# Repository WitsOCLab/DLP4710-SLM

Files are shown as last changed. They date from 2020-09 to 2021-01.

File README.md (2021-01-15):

# DLP4710-SLM
A 3D printed modification to the DLP4710EVM DMD to turn it into a lab-usable spatial light modulator. Optimised example MATLAB code for displaying Laguerre-Gauss holograms fullscreen are in the Examples folder.

**Created by:** Mitchell A. Cox in 2020 :: www.wits.ac.za/eie [mitchell.cox@wits.ac.za]

**License:** CC-BY-SA-4.0

## Reference

Please note that build instructions, photos, etc. are in the following paper:

M. A. Cox, A. V. Drozdov, "Converting a Texas Instruments DLP4710 DLP evaluation module into a spatial light modulator," Applied Optics, in press.

If you find this work useful, please consider citing or acknowledging it. If you make improvements, please send a pull request.

## 3D Printer Settings

The designs have been verified with an Ultimaker S3 using Cura with the following settings:

> **Layer height:** 0.1 mm
> **Infill:** 80%
> **Adhesion:** No
> **Support:** No
> **Material:** Black Strong PLA

**If you have been successful with other printers / settings, please let me know.**

## Errata / ProTips

* The DMD is quite a tight squeeze into the face-plate.

## Useful URLs

https://www.ti.com/tool/DLPDLCR4710EVM-G2

https://www.ti.com/tool/DLP4710EVM-LC

## Updating the Firmware

Some firmware updating is required so that the LEDs are disabled on start (otherwise it won't turn on as it thinks the LEDs are broken) and to set the input source to the HDMI port.

For some reason the Texas Instruments software for the DLP4710-G2 evaluation board doesn't update the firmware. It says it does, but it doesn't (it's pretty clear that nothing happens as it's too quick when one tries). Instead, the software meant for the DLP4710-LC must be used. It will complain about the wrong board, but it still works. The screenshot below shown the place where this should be done and how it looks.

A firmware image can be download from the TI product page. A batch file to switch off the LEDs and set the input is in the "Firmware" directory. Please note that if you try to flash the wrong firmware or if something goes wrong, it's at your own risk.

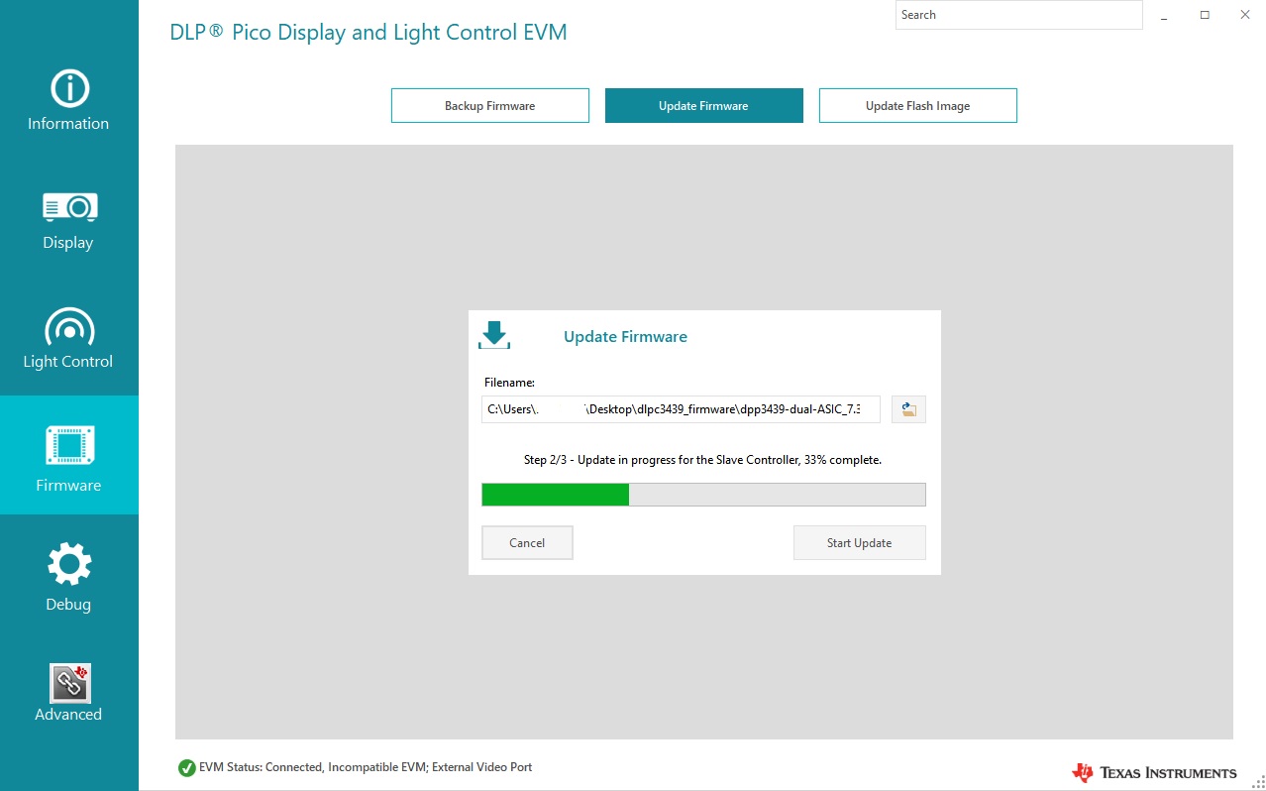
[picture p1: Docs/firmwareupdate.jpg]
DLP4710LC Update Screenshot


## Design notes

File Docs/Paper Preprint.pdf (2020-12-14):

Letter | Applied Optics | 1

# Converting a Texas Instruments DLP4710 DLP evaluation module into a spatial light modulator

MITCHELL A. COX1,* AND ALICE V. DROZDOV1

1School of Electrical and Information Engineering, University of the Witwatersrand, Johannesburg, South Africa *Corresponding author: mitchell.cox@wits.ac.za

Compiled December 14, 2020

Digital Micro-mirror Devices (DMDs) are a popular alternative to liquid crystal spatial light modulators for laser beam shaping due to their relatively low cost, high speed, as well as polarisation and wavelength independence. Here we describe in detail how to convert a low-cost digital light projector (DLP) evaluation module which uses a Texas Instruments DLP4710 DMD into a spatial light modulator using a 3D printed mount. The resulting device is shown to accurately shape Laguerre-Gauss modes, can operate in real-time over HDMI without modification with a 180 Hz hologram refresh rate, has a resolution of 1920×1080 pixels and a diagonal screen size of 0.47 inches.

http://dx.doi.org/10.1364/ao.XX.XXXXXX

### 1. INTRODUCTION

Digital Micro-mirror Devices (DMDs) were developed in the 1980s and 1990s and are now primarily used in digital movie projectors due to their high-contrast and high-power handling capabilities [1]. More recently, they have become a useful experimental tool that are now used in various optics experiments and applications such as structured light, microscopy, photolithography and single pixel imaging to name a few [2–8]. Here we focus on the use of DMDs as polarisation and wavelength invariant computer generated holograms for structured light applications such as mode creation and detection, wavefront sensing and polarimetry [9–14]. The presented arrangement, however, is such that the DMD may find use in many other applications.
A DMD is a 2D array of micro-mirrors spaced several micrometers apart with the ability to be electronically tilted to an “on” or “off” position, usually to direct incident light toward or away from a target [12]. The resolution of modern DMDs is on the order of hundreds or even thousands of pixels in each dimension. Typically, the available resolutions follow common display standards and so 1920×1080 (Full HD) is readily available, but higher and lower resolutions are available (at higher or lower cost).
In order to use a DMD as a so-called spatial light modulator, the bare DMD must be situated such that an incident laser beam and required experimental components can be conveniently

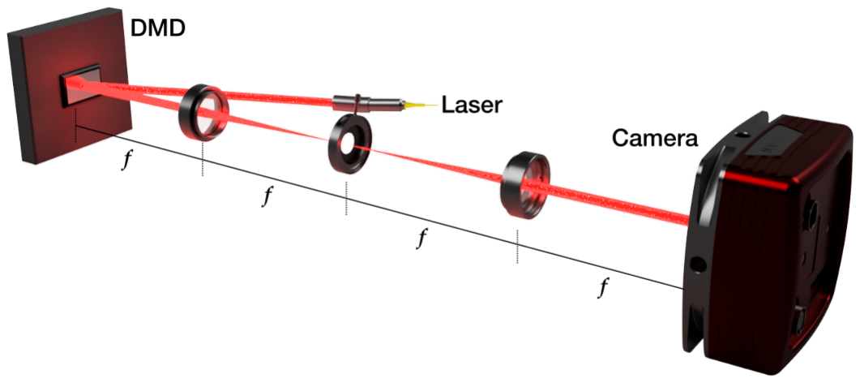
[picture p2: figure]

Fig. 1. A typical experimental layout with a single mode fibrebased laser source, a DMD, a spatial filter and a camera. For the demonstration tests presented here we used f = 100 mm lenses and a 635 nm single-mode coupled laser diode source collimated to a beam diameter of 2.1 mm.

located. Some DMD development modules are sold without optics such as the Texas Instruments DLP 6500 EValuation Modules (EVM) [15] and DLP Discovery 4100 Development Platform [16], and are usable with a custom mount and no further modification. Here we focus instead on the Texas Instruments DLPDLCR4710EVM-G2 which is significantly cheaper (and thus more accessible to researchers with a tighter budget) than other DMD evaluation modules currently available, while also having specifications highly conducive to structured light experiments [17]. A physically similar module, the DLP4710EVM-LC is also expected to work using the modifications described here [18]. Unfortunately, both DLP4710 EVM models have pre-installed projection optics which must be removed before they can be used.
In Sec. 2, a typical experimental setup for mode creation is provided, as well as a brief summary of how holograms for DMDs can be created with references to some tutorial papers for the interested reader. This setup and generation method is used to test the performance of the modified DLP4710 EVM with some test results also presented. Section 3 details the required modifications, 3D printed components and firmware configuration to use the DLP4710 EVM as a spatial light modulator.

### 2. SHAPING LIGHT WITH A DMD

Since the DMD can be re-purposed as a digital hologram, it can be used to structure light, with a comprehensive tutorial in

Ref. [12]. It is out of the scope of this paper to go into detail on the various possible techniques to do this, but for the purposes of demonstrating a working device, some brief background is given in this section.
A minimal experimental setup is shown in Fig. 1, where a collimated Gaussian laser beam is reflected off the DMD, where the first-order is then spatially filtered using a 4 f-system using an adjustable iris aperture and finally imaged using a camera. We use this setup to test and demonstrate the capabilities of the DLP4710 DMD, described in Sec. 4.
A DMD is an amplitude-only device and cannot inherently modulate the phase of light, which is required for complex beam shaping. In order to encode a field with both amplitude and phase components a special grating function is used to create a binary, amplitude-only hologram [12, 19]. The transmission function of this type of hologram is given by

T =

1
2

+

1
2

sgn

cos(2πψG + ψU) + cos

arcsin
A

Amax , (1)

where ψU and A/Amax are the phase and normalised amplitude of the desired complex field, U, respectively (for example Eq. 2, which describes a Laguerre-Gauss (LG) mode) and ψG is a linear phase ramp which defines the period of the resulting grating. Examples of what the binary holograms look like with LG modes are shown in Fig. 5 (a).
LG modes are solutions to the scalar Helmholtz equation in cylindrical coordinates [20]. They form an orthonormal basis and are also Eigenmodes of free-space, making them useful for long-distance propagation, for example in multiplexed wireless optical communication [21]. At the plane of the DMD (i.e z = 0) they are given by

U

LG
`,p

(r, φ) = C

LG

r

√
2
w0

!|`|
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
exp(−i`φ),

(2)
where ` and p are the azimuthal and radial mode indices respectively, w0 is the beam waist, C

LG is a normalisation constant and L

|`|
p (·) is the generalised Laguerre polynomial.
LG modes are identifiable as they appear as donut-shaped rings on a camera in a setup such as in Fig. 1. Larger azimuthal indices result in larger diameter rings and radial modes manifest as rings around the bright, central ring. Even small aberrations on the surface of the DMD will result in these rings becoming distorted. This is a convenient qualitative measure of the DMDs beam shaping performance.
If the resulting beam quality is insufficient, a correction phase can be added or subtracted to the hologram. The Gerchberg-Saxton algorithm can be used to find this phase, or alternatively, suitable Zernike phases can be added or subtracted in a “trialand-error” manner [10]. As a last resort, one can reduce the size of the encoded beams to limit the exposure to the aberrated area.

### 3. HARDWARE AND FIRMWARE

The DLP4710 DMD from Texas Instruments has an array size of 1920×1080 pixels with a pixel pitch of 5.4 µm. This results in an active array size of 10.4×5.8 mm (or 0.47 inch diagonal). The DMD is available on two affordable evaluation modules, both of which can be modified for laser-based experiments. In this work the DLPDLCR4710EVM-G2 was used, but the DLP4710EVM-LC appears to have the same dimensions as it seems that only a different chipset is used (See. Sec. C) [17, 18].

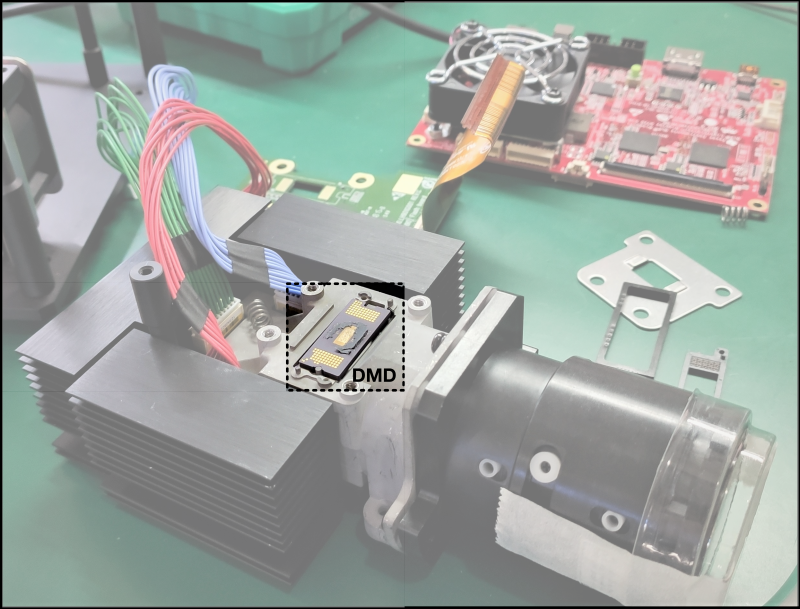
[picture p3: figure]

Fig. 2. A photo of the DLP4710 EVM with the main PCB removed, showing the un-soldered DMD positioned in the projection optics module.

The 3D printed assembly is described in Sec. 3A, as well as some firmware configuration changes, described in Sec. 3B. Holograms are displayed on the DMD via the HDMI connection, as the EVM simply shows up as another monitor. We describe how to display holograms at a rate of 180 Hz over HDMI in Sec. 3C.

A. 3D Printed Assembly
There are two reasons why a custom mounting assembly is required for the DLPDLCR4710EVM-G2. The first is that the bare DMD chip must be positioned vertically at a height that is suitable for standard laser-based setups. Unfortunately, the DLP4710 DMD is not soldered to the board in this EVM and so simply stripping away the projection optics is not an option. A precise assembly is thus required to hold all the components in alignment.
As is visible in Fig. 2, the DMD is precisely slotted into the projection optics and uses a spring-loaded inter-poser shim for the electrical signals to a PCB (Printed Circuit Board) which is screwed down with heat-sinks to hold everything in place. A precision assembly is therefore required to hold the DMD in place on the circuit board in the absence of the projection optics. A photo of the custom assembly is shown in Fig. 3 (a) and (d). Two plastic components must be printed at high resolution. Here an Ultimaker S3 at 0.1 mm layer height with “Strong PLA” filament and 80% infill was used to create a rigid and accurate structure. Figure 3 (b) shows the mount plate, which holds everything in position and allows for a standard M6 cap screw and optical post to be attached. Figure 3 (c) shows the more intricate cover plate, which has “pins” to hold the DMD, shim and PCB in precise alignment. No additional screws or hardware are required as the design is such that the existing screws and springs from the EVM can be used, as shown. The design caters for M3 nuts on the front of the cover plate for added strength and reliability, if required. The design files in both STEP and STL formats are available online [22].

To assemble, carefully slot the DMD face-down into the cover plate, then the shim and then place the PCB. Everything should slot into place. The square-shaped metal plate is placed behind

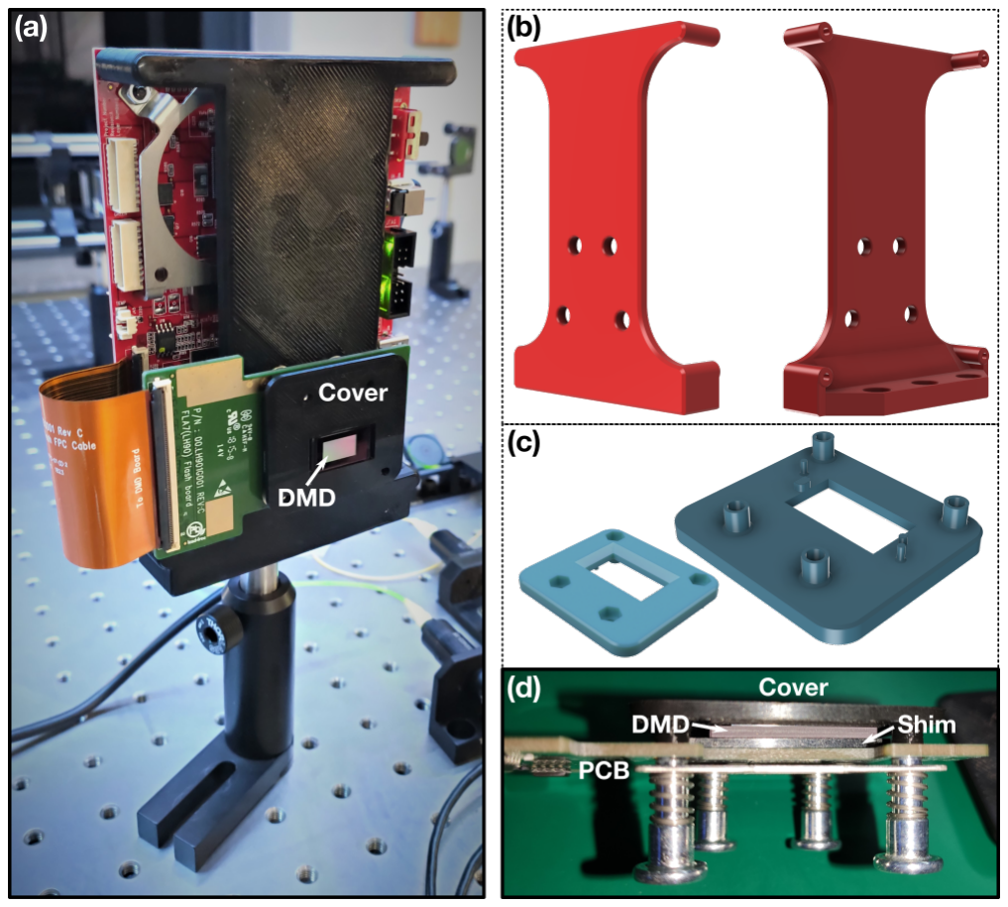
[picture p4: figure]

Fig. 3. A photo of the completed unit (a), with renderings of the 3D printed mount (b) and DMD cover (c). The key component is the cover, which has several alignment pins to hold the DMD, inter-poser shim and PCB in exact position (d).

the PCB, as it was before the DMD was removed from the light engine. Figure 3 (d) shows the resulting arrangement. In reality, the assembly requires the screws to be inserted through the mount plate (Figure 3 (b)) first, after which the springs are placed. While holding everything together in position, gently and carefully turn the screws so that they grab the cover plate. Incrementally tighten diagonally opposite screws until the assembly is rigid.
Do not over-tighten these screws as the plastic can be stripped. There is also a possibility that the DMD is warped if things are too tight, but the use of the shim largely prevents this, ensuring optical flatness. It should also be noted that there is a specified maximum clamping load of 110 N (Sec. 6.9 in the DLP4710 datasheet), but we are unable to verify this and assume that this load is not exceeded as the original clamping springs are used. Remove the fan from the top of the main board. This is not required as the LED driver circuit will not generate any heat with no LEDs connected. There should now be space to mount the cover assembly to the main PCB. Use the remaining screws to assemble everything as shown in Figure 3 (a). During this entire procedure, be careful of electrostatic discharge. A grounded wrist strap is recommended, and working on a grounded metal table or anti-static matt is also a good idea.
B. Firmware Configuration
By default, the firmware expects there to be LEDs connected. The module will not power on correctly if it detects that these LEDs are not present. In addition, the default mode of the device is to display a demo graphic and so this must be changed to the HDMI input. Fortunately, the configuration can be modified and saved into non-volatile memory.
Download and install the configuration utility from the DLP4710EVM product page [17]. Instructions are available from Texas Instruments to do this, and how to troubleshoot any issues that may arise. Using the utility, a so-called “batch file” can be created and flashed to the EVM to update the configuration on

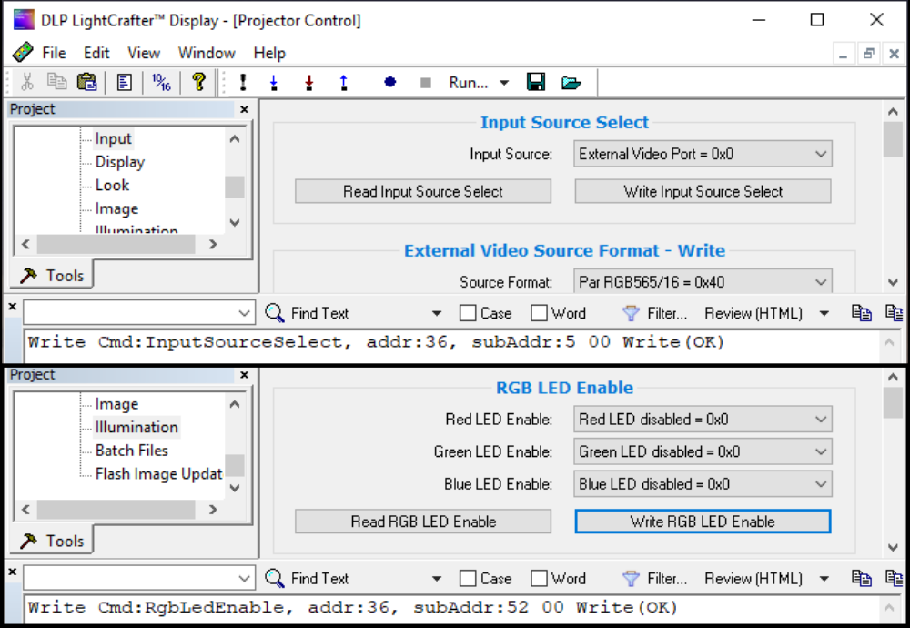
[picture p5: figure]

Fig. 4. Screenshots of the configuration utility in Advanced mode showing the HDMI source selection (top) and LED disable configuration (inset bottom).

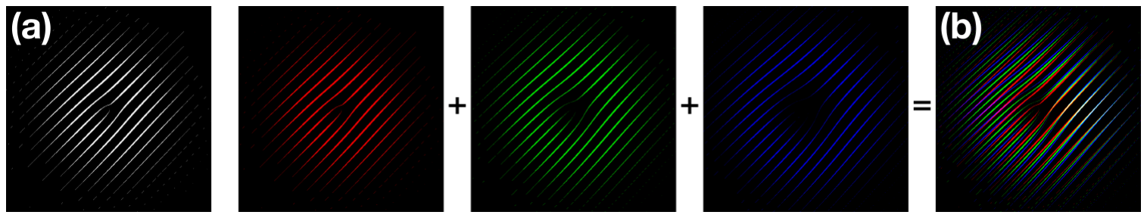
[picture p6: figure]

Fig. 5. (a) A typical binary hologram for a DMD of an LG,
` = 1 hologram for up to 60 Hz operation over HDMI. (b) The resulting hologram image with three consecutive LG holograms with ` = 1, 2 and 3 for 180 Hz operation.

startup.
The contents of this batch file, which is simply a text file with the extension “.bf”, are shown in Lst. 1. The specifics of how to install this file into non-volatile memory is left to the reader as the instructions are available from the manufacturer. For convenience, Fig. 4 shows a series of screenshots of the configuration utility highlighting the LED and input source configuration which can be done after the DMD is turned on, if the batch file method is not desired.
1 | # Write : InputSourceSelect
2 | W 36 05 00
3 | # Write : RgbLedEnable
4 | W 36 52 00
Listing 1. Batch file contents for the DLPDLCR4710EVM-G2 to disable the LEDs and switch to the HDMI input.
C. High Speed Display over HDMI
The specified frame-rate of the DLP4710 EVMs is 60 Hz over HDMI, and so holograms can be displayed at this rate without any special techniques. As an aside, the DLP4710 DMD itself supports 120 Hz and so the 60 Hz limitation is due to the chipset and firmware. Screen tearing or missed frames might occur at rates close to this frequency unless synchronisation to the screen refresh rate is used. Techniques to do this depend on the software and operating system and will not be detailed here. With an understanding of how the DMD modulates the Red (R), Green (G) and Blue (B) channels for 24 bit colour, we can in fact display different binary holograms at a rate of 180 Hz or even 1440 Hz [23]. Here we describe how to update the DMD at 180 Hz as no special configuration is required to do so. It should be noted that some DMD EVMs support the loading

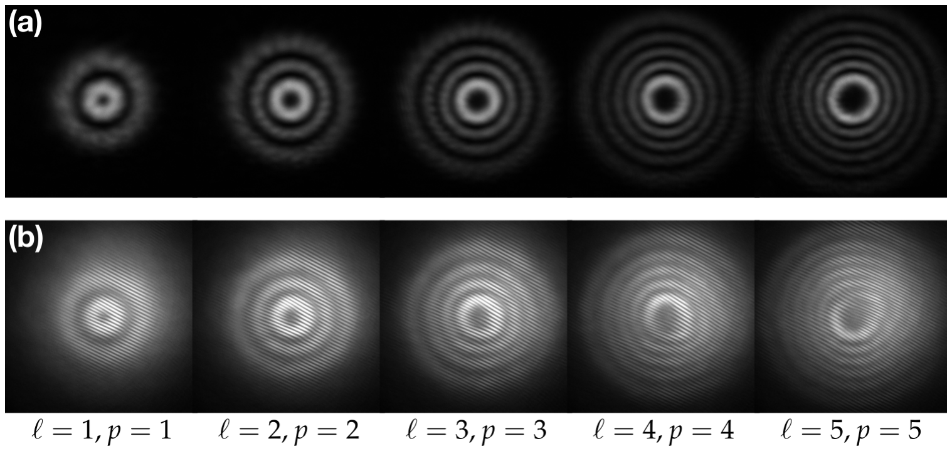
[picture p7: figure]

Fig. 6. (a) Example LG beams generated using the device with slight aberrations visible as deviations from a round shape confirmed by (b) which are Mach-Zehnder interferograms of the beams showing some curvature of the fringes and vortex splitting. The intensity variations in (a) are due to a suboptimal grating period and possibly some interference with the zero-order, which could be removed with a smaller spatial filter.

of images into the DMDs memory and playing them back at several kilohertz. This mode of operation is not supported on the DLPDLCR4710EVM-G2.
The DMD rapidly switches between the red, green and blue channels while synchronously toggling the corresponding coloured LEDs, to create the perception of a colour image. A black and white image is in fact displayed as three separate, sequential frames: the first is black and red, then black and green and finally black and blue. By encoding different holograms (or images) as each of these three colours and then merging them into a single image, the resulting “effective” rate is 180 Hz (if these images are displayed at 60 Hz). Figure 5 (b) diagrammatically shows what the displayed hologram might look like. As an example, Lst. 2 shows the MATLAB code to generate this RGB image from three binary images, since colour images in MATLAB are represented as 3D matrices. Example code for demonstrating this technique, as well as for displaying these colour images full screen as holograms on the EVM, is provided online [22].
1 | function [ imgCombined ] = Combine180 ( imgA , imgB , imgC )
2 | imgCombined = cat (3 , imgA , imgB , imgC );
3 | end
Listing 2. Generating a combined image to achieve 180 Hz hologram rate.

### 4. TEST RESULTS AND DISCUSSION

In order to perform a rudimentary test of the performance of this DMD, LG modes were generated with ` ∈ [−5, 5] and p ∈ [0, 5], with the code available online [22], using a similar setup to that given in Fig. 1. The incoming beam had a 1/e

2 diameter of
2.1 mm and the encoded beams had w0 = 1 mm.
The holograms for each mode were generated, displayed on the DMD and then the resulting beam was captured with a camera. These images were inspected and the modes are high quality. Figure 6 (a) shows a selection of images of these modes. Some distortion is visible on the largest mode, indicative of minor aberrations.
This is confirmed by the interferograms shown in Fig. 6 (b), generated by interfering the incoming Gaussian beam with the resulting mode. The fringes on the interferograms should be straight, with a fork at the centre with a number of “tines” depending on `. Some curvature is visible as well as some vortex splitting. While taking these measurements we noted that the mount is quite sensitive to vibrations. This is due to the vertical arrangement and the low rigidity of the plastic. The design was modified to increase the rigidity and in future versions we plan to improve it further.
We speculate that the relatively insignificant aberrations of this particular DMD (compared to the DLP6500 used by one of the authors previously [9]) are due to two reasons. The first is it’s relatively small size which limits bending. Second, we believe that the main reason for the high flatness of this DMD is because it is not soldered down. It is possible that the process of soldering the DMD causes differential expansion and contraction as the solder cools, deforming the DMD. In a projection setup these aberrations would be of no consequence, but for beam shaping a fraction of the wavelength has an impact.
High speed operation at 180 Hz was also verified by combining three different LG beams into a single RGB image and observing the laser beam using a camera running at 500 Hz. Unfortunately there is no output trigger signal on the DLPDLCR4710EVM-G2 which could have been used to trigger the camera in sync to the frame changes, and so oversampling was necessary. If this signal is required, it is available on the DLP4710EVM-LC, according to the datasheet.

### 5. SUMMARY

Spatial light modulators have become a staple component in laser optics labs working with structured light. Digital micromirror devices are versatile, fast and affordable and are an excellent alternative to conventional liquid crystal spatial light modulators. DMDs are not yet available as off-the-shelf as scientific instruments and so evaluation kits usually in the form of digital projectors must be purchased and modified.
We explain in detail how the Texas Instruments DLP4710 evaluation modules can be modified for laser beam shaping with some 3D printed components and firmware configuration. We visually tested the resulting device with a range of LG modes and find the device to be remarkably aberration-free.

FUNDING

The authors would like to acknowledge South African National Research Foundation grant 121908 and the National Laser Centre Rental Pool program.
Disclosures. The author declares no conflicts of interest.

REFERENCES

1. L. J. Hornbeck, “Multi-level deformable mirror device,” (1992). US Patent 5,083,857.
2. T. M. Kreis, P. Aswendt, and R. Höfling, “Hologram reconstruction using a digital micromirror device,” Opt. Eng. 40, 926–933 (2001).
3. D. Dan, M. Lei, B. Yao, W. Wang, M. Winterhalder, A. Zumbusch,
Y. Qi, L. Xia, S. Yan, Y. Yang et al., “DMD-based led-illumination super-resolution and optical sectioning microscopy,” Sci. Rep. 3, 1116 (2013).
4. A. Sandmeyer, M. Lachetta, H. Sandmeyer, W. Hübner, T. Huser, and M. Müller, “DMD-based super-resolution structured illumination microscopy visualizes live cell dynamics at high speed and low cost,” bioRxiv p. 797670 (2019).
5. K. V. Vienola, M. Damodaran, B. Braaf, K. A. Vermeer, and J. F. de Boer, “Parallel line scanning ophthalmoscope for retinal imaging,” Opt. Lett. 40, 5335–5338 (2015).

6. M. P. Edgar, G. M. Gibson, and M. J. Padgett, “Principles and prospects for single-pixel imaging,” Nat. Photonics 13, 13–20 (2019).
7. Z. Xiong, H. Liu, R. Chen, J. Xu, Q. Li, J. Li, and W. Zhang, “Illumination uniformity improvement in digital micromirror device based scanning photolithography system,” Opt. Express 26, 18597–18607 (2018).
8. Y. Zhang, J. Luo, Z. Xiong, H. Liu, L. Wang, Y. Gu, Z. Lu, J. Li, and J. Huang, “User-defined microstructures array fabricated by DMD based multistep lithography with dose modulation,” Opt. Express 27 ,
31956–31966 (2019).
9. M. A. Cox, E. Toninelli, L. Cheng, M. J. Padgett, and A. Forbes, “A High-Speed, Wavelength Invariant, Single-Pixel Wavefront Sensor With a Digital Micromirror Device,” IEEE Access

7, 85860–85866 (2019).
10. J. Pinnell, I. Nape, B. Sephton, M. A. Cox, V. Rodriguez-Fajardo, and
A. Forbes, “Modal analysis of structured light with spatial lightmodulators: a practical tutorial,” J. Opt. Soc. Am. A 37, 146–160 (2020).
11. K. Singh, N. Tabebordbar, A. Forbes, and A. Dudley, “Digital Stokes polarimetry and its application to structured light: tutorial,” J. Opt. Soc. Am. A 37, C33 (2020).
12. S. Scholes, R. Kara, J. Pinnell, V. Rodríguez-Fajardo, and A. Forbes, “Structured light with digital micromirror devices: a guide to best practice,” Opt. Eng. 59, 1 (2019).
13. S. Turtaev, I. T. Leite, K. J. Mitchell, M. J. Padgett, D. B. Phillips, and T. Cižmár, “Comparison of nematic liquid-crystal and DMD based ˇ spatial light modulation in complex photonics,” Opt. Express 25, 29874– 29884 (2017).
14. C. Rosales-Guzmán, X. B. Hu, A. Selyem, P. Moreno-Acosta, S. Franke-Arnold, R. Ramos-Garcia, and A. Forbes, “Polarisation-insensitive generation of complex vector modes from a digital micromirror device,” Sci. Rep. 10, 1–9 (2020).
15. Texas Instruments, “DLP

® LightCrafter
™ 6500 Evaluation Module,” https://www.ti.com/tool/DLPLCR6500EVM. Accessed 2020-09-07.
16. Texas Instruments, “DLPD4X00KIT DLP

® Discovery 4100 Development Platform,” https://www.ti.com/tool/DLPD4X00KIT. Accessed 2020-09-07.
17. Texas Instruments, “DLPDLCR4710EVM-G2 DLP

® 4710 Light control
evaluation module,” https://www.ti.com/tool/DLPDLCR4710EVM-G2 .
Accessed 2020-09-07.
18. Texas Instruments, “DLP4710EVM-LC DLP

® 4710 Light control evaluation module,” https://www.ti.com/tool/DLP4710EVM-LC. Accessed 2020-09-07.
19. W.-H. Lee, “Binary synthetic holograms,” Appl. Opt. 13, 1677–1682 (1974).
20. M. A. Cox, N. Mphuthi, I. Nape, N. Mashaba, L. Cheng, and A. Forbes, “Structured Light in Turbulence,” IEEE J. Sel. Top. Quantum Electron. 27, 1–21 (2021).
21. A. Trichili, M. A. Cox, B. S. Ooi, and M.-S. Alouini, “Roadmap to free space optics,” J. Opt. Soc. Am. B 37, A184 (2020).
22. M. A. Cox, “DLP4710-SLM GitHub Repository,” https://github.com/WitsOCLab/DLP4710-SLM. (https://github.com/WitsOCLab/DLP4710-SLM) Accessed 2020-09-07.
23. M. Wexler, “Using the Texas Instruments DLP4710EVM-LC for generating visual stimuli at 180 and 1440 Hz,” http://lab-perception.org/dlp4710/. (http://lab-perception.org/dlp4710/) Accessed 2020-09-07.

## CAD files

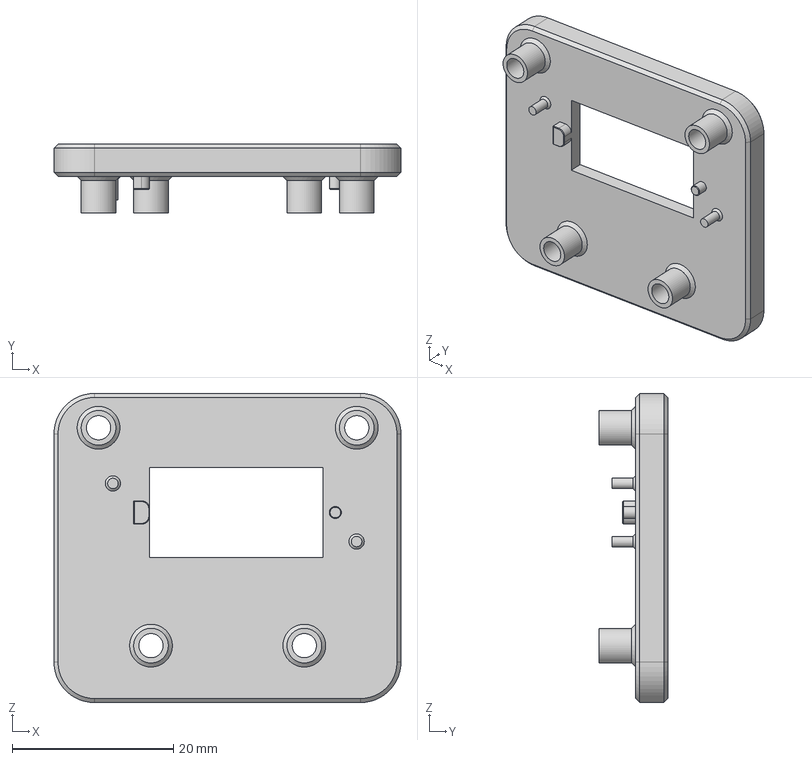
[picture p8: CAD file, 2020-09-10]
DLP4710CoverPlate.step
43.0 x 8.50 x 38.3 mm

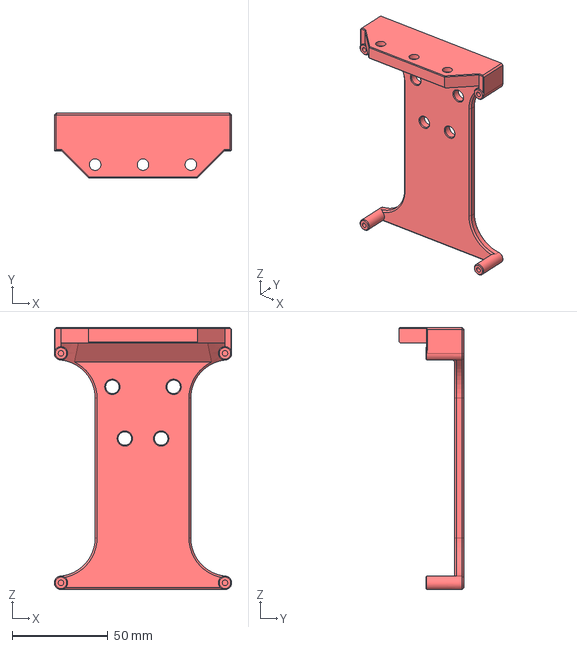
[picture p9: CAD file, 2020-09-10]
DLP4710MountPlate.step
92.7 x 34.0 x 136.9 mm

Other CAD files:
DLP4710CoverPlate.f3d
DLP4710CoverPlate.stl
DLP4710MountPlate.f3z
DLP4710MountPlate.stl

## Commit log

2020-12-14 new cover plate design
    [DLP4710CoverPlate.stl]
2021-04-05 Create LEDHDMI-LC.bf
    for the DLP4710-LC, use external pattern mode rather than HDMI input.
